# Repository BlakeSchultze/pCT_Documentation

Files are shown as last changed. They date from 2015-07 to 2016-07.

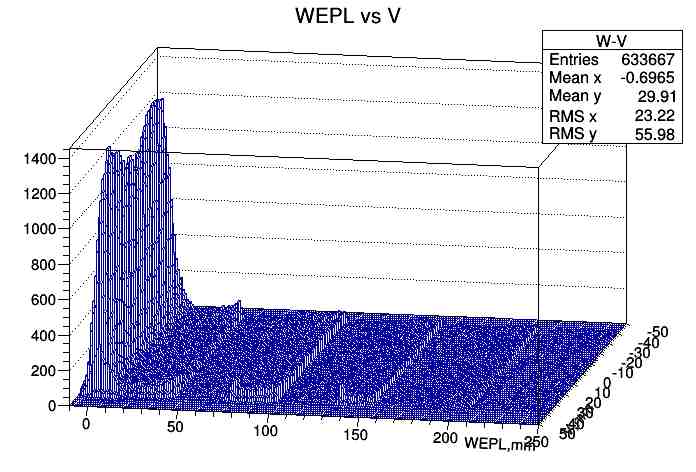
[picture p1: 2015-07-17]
Experimental_pCT_Runs/May 2015/preprocessing/WvsV1-1-1-1-4.5.jpg

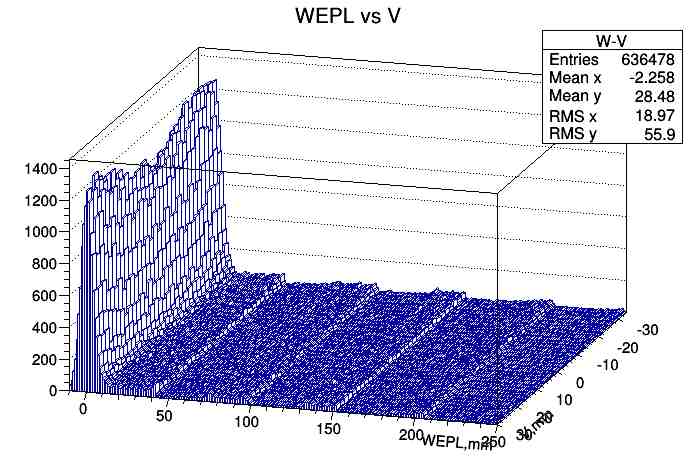
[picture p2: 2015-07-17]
Experimental_pCT_Runs/May 2015/preprocessing/WvsV1-2-3-4-5.jpg

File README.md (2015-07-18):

# pCT-Collaboration-Documents
======================================================
pCT Collaboration Document Sharing
======================================================
Contains the documentation associated with the pCT project such as descriptions of the scanner system and its operation as well as the various objects/phantoms that have or will be scanned.  This repository also includes the these/dissertations of students who worked on the project and publications from members of the collaboration or other outside groups on the subject of pCT or closely related topics.

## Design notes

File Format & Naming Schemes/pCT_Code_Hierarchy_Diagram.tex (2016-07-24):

%\newgeometry{left=1.25in,top=1.0in,bottom=-2in, paperwidth=4.3in,paperheight=4.4in,centering}
%top color=blue!2!white, middle color=blue!6!white, bottom color=blue!13!white
%\clearpage%
\Section{pCT\_code Hierarchy Diagram}[the diagram below shows the hierarchy of \docentry[constdir]{pCT\_code} directories including those containing clones of the GitHub accounts/repositories relevant to pCT.]%
\centering%
\begin{tikzpicture}[scale=4, font=\small,framed,background rectangle/.style={double, ultra thick, draw=stdblue, double=cyan, top color=stdblue!1!white, rounded corners=20pt}]
\matrix[row sep=4mm,column sep=2mm]
{%
&\node(parentdot)[pt]{};\\
&\node(01)[D]{ion};\\
&\node(11)[D]{pCT\_code};\\
\node(20)[pt]{};&\node(21)[pt]{};&&\node(23)[pt]{};\\
\node(30)[D]{user\_code};    &&&\node(33)[D]{git};\\[0mm]
%\node(01)[pt]{};&\node(top3)[pt]{};&\node(03)[pt]{};&&&\node(04)[pt]{};&&&\node(05)[pt]{};\\
\node(40)[D]{$<$username$>$};&\node(41)[pt]{};&\node(42)[pt]{};&\node(43)[pt]{};&&\node(45)[pt]{};\\
&\node(51)[D]{BlakeSchultze};&\node(52)[D]{BaylorICTHUS};&&&\node(55)[D]{pCT-collaboration};\\[1mm]
\node(60)[pt]{};&\node(61)[pt]{};&\node(62)[F]{pCT\_Reconstruction};&\node(63)[pt]{};&\node(64)[pt]{};&\node(65)[pt]{};&\node(66)[pt]{};&\node(67)[pt]{};\\[1mm]
\node(70)[F]{pCT\_Reconstruction};&\node(71)[F]{pCT\_Documentation};&&\node(73)[F]{pCT-docs};&\node(74)[F]{pCT\_Tools};&\node(75)[F]{Reconstruction\_BU};&\node(76)[F]{pct-recon-copy};&\node(77)[F]{Preprocessing};\\[1mm]
};
%\path[every node/.style={font=\sffamily\small}]
%       (parentdot) edge node (01)
%       (01) edge node {} (11)
%       (11) edge node {} (21)
%       (21) edge node {} (20)
%       (20) edge node {} (30)
%       (30) edge node {} (40);%
%%       (B) 	edge [loop left] node {0.0} (B)
%%           	edge [bend right] node [right] {0.0} (D)
%%           	edge [bend right] node[below] {0.0} (C)
%%       (C) 	edge [bend right] node [right] {0.0} (A)
%%           	edge [bend right] node [above] {0.0} (B)
%%           	edge [bend left] node [left] {0.0} (D)
%%           	edge [right] node [above] {0.0} (E)
%%       (D) 	edge [loop below] node {0.0} (D);
\graph [use existing nodes, edge label]
{
(parentdot)->(01)->(11)->(21)--(20)->(30)->(40);
(21)--(23)->(33)--(43)--(42)--(41)->(51)--(61)--(60)->(70);
(43)--(45)->(55)--(65)--(63)--(67)->(77);
(42)->(52)->(62);
(61)->(71);
(63)->(73);
(64)->(74);
(65)->(75);
(66)->(76);
};
\end{tikzpicture}
\endinput

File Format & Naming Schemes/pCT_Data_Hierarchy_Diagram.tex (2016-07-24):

\clearpage%
\Section{organized\_data Hierarchy Diagram}[the diagram below shows the hierarchy of \docentry[constdir]{organized\_data} directories where the vertical ellipses (\,$\vdots$\,) indicate the subdirectories of the experimental and simulated data scan date directories are identical.]
\centering%
%\newgeometry{left=1.25in,top=1.0in,bottom=-2in, paperwidth=4.3in,paperheight=4.4in,centering}
%top color=blue!2!white, middle color=blue!6!white, bottom color=blue!13!white
\begin{tikzpicture}[scale=4, framed,background rectangle/.style={double, ultra thick, draw=stdblue, double=cyan, top color=stdblue!1!white, rounded corners=20pt}]
\matrix[row sep=4mm,column sep=1mm]
{%
	&&&\node(parentdot)[pt]{};&&&&\\
	&&&\node(parentdir)[D]{ion};&&&&\\
	&&&\node(pctdata)[D]{pCT\_data};&&&&\\
	&&&\node(organizeddata)[D]{organized\_data};&&&&\\
	&\node(top1)[pt]{};&&\node(top3)[pt]{};&\node(top4)[pt]{};&&&\\
	&\node(001)[D]{Experimental};    &&&\node(004)[D]{Simulated};&\\[-2mm]
	&\node(01)[pt]{};&&\node(03)[pt]{};&\node(04)[pt]{};&\node(05)[pt]{};&&\\
	&\node(11)[D]{YY-MM-DD};        &&\node(13)[D]{G\_YY-MM-DD};&&\node(15)[D]{T\_YY-MM-DD};\\[1mm]
	&&&\node(0023)[textonly]{$\vdots$};&&\node(0025)[textonly]{$\vdots$};&&\\[-13mm]
	%&&&&&\\[-5mm]
	&\node(21)[D]{XXXX[\_AAA]};     &&\node(23)[textonly]{};&&\node(25)[textonly]{};\\[0mm]
	\node(30)[pt]{};&\node(31)[pt]{}; & \node(32)[pt]{};&&&\\
	\node(40)[D]{Input};       &&\node(42)[D]{Output};       &&&&\\
	\node(50)[F]{raw\_xxx.bin};&&\node(52)[D]{YY-MM-DD};     &&&&\\[-2mm]
	&\node(61)[pt]{};          &\node(62)[pt]{};    &\node(63)[pt]{};&\node(64)[pt]{};&\node(65)[pt]{};\\
	&\node(71)[F]{Wcalib.txt}; &\node(72)[D]{Reconstruction}; &\node(73)[F]{TVcorr.txt};   &\node(74)[F]{WcalibTemp.txt};&\node(75)[F]{projection\_xxx.bin};&&&&&&&&\\[-2mm]
	&				   &\node(82)[pt]{};&\node(83)[pt]{};&\\
	&                          &\node(92)[D]{YY-MM-DD};       &\node(93)[F]{settings.cfg};&&&&&&&&&&\\[-2mm]
	\node(100)[pt]{};&\node(101)[pt]{};&\node(102)[pt]{};    &\node(103)[pt]{};&\node(104)[pt]{};&\node(105)[pt]{};\\
	\node(110)[F]{hull.txt};&\node(111)[F]{FBP.txt};&\node(112)[D]{Images};&\node(113)[F]{x\_0.txt};&\node(114)[F]{TV\_measurements.txt};&\node(115)[F]{execution\_log.txt};
	&&&&&&&&\\
	&& \node(122)[D]{YY-MM-DD};\\[-2mm]
	&\node(131)[pt]{};&\node(132)[pt]{};&\node(133)[pt]{};&&\\
	&\node(141)[F]{x\_k.dcm};&\node(142)[F]{x\_k.txt};&\node(143)[F]{x\_k.png};&&&&&&&&&&\\
};
\graph [use existing nodes, edge label]
{
	(parentdot)->(parentdir)->(pctdata)->(organizeddata)--(top3)--(top1)->(001)--(01)->(11)->(21)--(31)--(30)->(40)->(50);
	(top3)--(top4)->(004)--(04)--(05)->(15)->(25);
	(04)--(03)->(13)->(23);
	(31)--(32)->(42)->(52)--(62)->(72)--(82)->(92)--(102)->(112)->(122)--(132)->(142);
	(61)--(62)--(63)--(64)--(65);
	(61)->(71);
	(62)->(72);
	(63)->(73);
	(64)->(74);
	(65)->(75);
	(82)--(83)->(93);
	(100)--(101)--(102)--(103)--(104)--(105);
	(100)->(110);
	(101)->(111);
	(102)->(112);
	(103)->(113);
	(104)->(114);
	(105)->(115);
	(131)--(132)--(133);
	(131)->(141);
	(132)->(142);
	(133)->(143)
};
\end{tikzpicture}
\endinput

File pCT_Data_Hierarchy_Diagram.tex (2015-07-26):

\documentclass[landscape,a4]{article}
\usepackage{mymacros}
%%%%%%%%%%%%%%%%%%%%%%%%%%%%%%%%%%%%%%%%%%%%%%%%%%%%%%%%%%%%%%%%%%%%%%%%%%%%%%%%%%%%%%%%%%%%%%%%%%%%%%%%%%%%%%%%%%%%%%%%%%%%%%%%%%%%%%%%%%%%%%%%%%%%%%%%%%%%%%%%%%%%%%%%%%%%%%%%%%%%%%%%%%%%%%%%%%%%%%%%%%%%%%%%%%%%%%%%%%%%%%
%%%%%%%%%%%%%%%%%%%%%%%%%%%%%%%%%%%%%%%%%%%%%%%%%%%%%%%%%%%%%%%%%%%%%%%%%%%%%%%%%%%%%%%%%%%%%%%%%%%% Document Body %%%%%%%%%%%%%%%%%%%%%%%%%%%%%%%%%%%%%%%%%%%%%%%%%%%%%%%%%%%%%%%%%%%%%%%%%%%%%%%%%%%%%%%%%%%%%%%%%%%%%%%%%%%
%%%%%%%%%%%%%%%%%%%%%%%%%%%%%%%%%%%%%%%%%%%%%%%%%%%%%%%%%%%%%%%%%%%%%%%%%%%%%%%%%%%%%%%%%%%%%%%%%%%%%%%%%%%%%%%%%%%%%%%%%%%%%%%%%%%%%%%%%%%%%%%%%%%%%%%%%%%%%%%%%%%%%%%%%%%%%%%%%%%%%%%%%%%%%%%%%%%%%%%%%%%%%%%%%%%%%%%%%%%%%%
\begin{document}
%%%%%%%%%%%%%%%%%%%%%%%%%%%%%%%%%%%%%%%%%%%%%%%%%%%%%%%%%%%%%%%%%%%%%%%%%%%%%%%%%%%%%%%%%%%%%%%%%%%%%%%%%%%%%%%%%%%%%%%%%%%%%%%%%%%%%%%%%%%%%%%%%%%%%%%%%%%%%%%%%%%%%%%%%%%%%%%%%%%%%%%%%%%%%%%%%%%%%%%%%%%%%%%%%%%%%%%%%%%%%%
%%%%%%%%%%%%%%%%%%%%%%%%%%%%%%%%%%%%%%%%%%%%%%%%%%%%%%%%%%%%%%%%%%%%%%%%%%%%%%%%%%%%%%%%%% Create Title Page With Graphics %%%%%%%%%%%%%%%%%%%%%%%%%%%%%%%%%%%%%%%%%%%%%%%%%%%%%%%%%%%%%%%%%%%%%%%%%%%%%%%%%%%%%%%%%%%%%%%%%%%
%%%%%%%%%%%%%%%%%%%%%%%%%%%%%%%%%%%%%%%%%%%%%%%%%%%%%%%%%%%%%%%%%%%%%%%%%%%%%%%%%%%%%%%%%%%%%%%%%%%%%%%%%%%%%%%%%%%%%%%%%%%%%%%%%%%%%%%%%%%%%%%%%%%%%%%%%%%%%%%%%%%%%%%%%%%%%%%%%%%%%%%%%%%%%%%%%%%%%%%%%%%%%%%%%%%%%%%%%%%%%%
\tikzset{fontscale/.style = {font=\relsize{#1}}
    }
    \begin{tikzpicture}[
%%%%%%%%%%%%%%%%%%%%%%%%%%%%%%%
D/.style={
% The shape:
rectangle,
% The size:
minimum size=1pt,
% The border:
very thick,
draw=green!50!black!50, % 50% red and 50% black,
% and that mixed with 50% white
% The filling:
top color=white, % a shading that is white at the top...
bottom color=green!50!black!20, % and something else at the bottom
% Font
font=\itshape\tiny
},
%%%%%%%%%%%%%%%%%%%%%%%%%%%%
F/.style={
% The shape:
rectangle,
rounded corners=5pt,
% The size:
minimum size=1mm,
% The border:
very thick,
draw=green!50!black!50, % 50% red and 50% black,
% and that mixed with 50% white
% The filling:
top color=white, % a shading that is white at the top...
bottom color=blue!50!black!20, % and something else at the bottom
% Font
font=\itshape\tiny
},
%%%%%%%%%%%%%%%%%%%%%%%%%%%%%%
end/.style={
% The shape:
rectangle,
rounded corners=5pt,
% The size:
minimum size=4mm,
% The border:
very thick,
draw=green!50!black!50, % 50% red and 50% black,
% and that mixed with 50% white
% The filling:
top color=white, % a shading that is white at the top...
bottom color=red!50!black!20, % and something else at the bottom
% Font
font=\itshape\tiny
},
%%%%%%%%%%%%%%%%%%%%%%%%%%%%%%%%%%%%%%%%
,>=stealth',thick,black!50,text=black,
every new ->/.style={shorten >=0pt},
graphs/every graph/.style={edges=rounded corners},
%%%%%%%%%%%%%%%%%%%%%%%%%%%%%%%%%%%%%%%%%%%%%%%%%%%%%%%%%
pt/.style={draw,inner sep=0pt,minimum size=0.3pt,fill=black!50},
%%%%%%%%%%%%%%%%%%%%%%%%%%%%%%%%%%%%%%%%%%%%%%%%%%%%%%%%%%%%%%%%%%%
skip loop/.style={to path={-- ++(0,#1) -| (\tikztotarget)}}]
\matrix[row sep=3mm,column sep=1mm]
{\tiny
                           &&&&&&&\node(013)[D]{pCT Data};    &&&&&&                       &&\\[0mm]
                           &&\node(20)[pt]{};                 &&&&&&&\node(213)[pt]{};     &&&&&&\node (23)[pt]{};            &&\\
                           &\node(30)[D]{Experimental};       &&&&&&&                      &&&&&&\node(33)[D]{Simulated};   &&\\
                           &\node(40)[D]{YY-MM-DD(Run Date)}; &&&&&&&                      &&&&&&&&\\[-1mm]
                           &\node(50)[D]{XXXX[\_AAA](Run\#)}; &&&&&&&                      &&&&&&&&\\
\node(60)[D]{Input};       &&\node(50)[D]{Output};            &&&&&&&                      &&&&&&&&\\
\node(60)[F]{raw\_xxx.bin};&&\node(50)[D]{YY-MM-DD};          &&&&&&&                      &&&&&&&&\\
&\node(60)[F]{Calib.txt};  &\node(50)[F]{projection\_xxx.bin};&\node(613)[F]{settings.cfg};&\node(613)[D]{Reconstruction};&&&&&&&&\\
&                          &                                  &                            & \node(613)[D]{YY-MM-DD};  &&&&&&&&&\\
&\node(50)[F]{hull.txt};   &\node(613)[F]{FBP.txt};           &\node(613)[F]{x\_0.txt};    &\node(613)[F]{MLP.bin};    &\node(613)[F]{histories.bin};&\node(50)[D]{Images};&&&&&&&\\
&                          &                                  &                            &                           &                            & \node(613)[D]{YY-MM-DD}; &&&&&;            &&\\
&                          &                                  &                            &                           & \node(613)[F]{DICOM};   & \node(613)[F]{TEXT}; &\node(613)[F]{PNG};&&&&;            &&\\
};
%\matrix[row sep=5mm,column sep=1mm]
%{
%    \node (t) [task] {Established Tasks};\\
%    \node (d) [development] {Newly ProposedIn Development};\\
%    \node (r) [remove] {Potentially Replace};
%};
\graph [use existing nodes, edge label]
{
};

\end{tikzpicture}

\end{document}

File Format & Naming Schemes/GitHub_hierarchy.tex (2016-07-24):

%\clearpage%
\Section{GitHub Accounts/Repositories}
\begin{tcbenvironment}'tcbBlueStyle'[title=\shadowText{GitHub}]
%%%%%%%%%%%%%%%%%%%%%%%%%%%%%%%%%%%%%%%%%%%%%%%%%%%%%%%%%%%%%%%%%%%%%%%%%%%%%%%%%%%%%%%%%%%%%%%%%%%%%%%%%%%%%%%%%%%%%%%%%%%%%%%%%%%%%%%%%%%%%%%%%%%%%%%%%%%%%%%%%%%%%%%%%%%%%%%%%%%%%%%%%%%%%%%%%%%%%%%%%%%%%%%%%%%%%%%%%%%%%%
\begin{tcbparagraph}'tcbBlueStyle'(title=https:\dirsep\dirsep github.com\dirsep\caratenclosed*{GitHub account}\dirsep\caratenclosed*{GitHub repository})
$\boldsymbol{-}$ below is an outline of the GitHub accounts and repositories containing the source code for the various tools and programs relevant to pCT and the documentation for pCT software/hardware, code/data storage and management, collaborator projects and contact information, phantom naming and properties, and other useful information for pCT users.  To provide users with easy/direct access to the source code in these repositories, they are cloned to Kodiak/Tardis and stored according to the organizational scheme shown in \autohyperlink[type=Section]{Code Organization}.
\end{tcbparagraph}
%%%%%%%%%%%%%%%%%%%%%%%%%%%%%%%%%%%%%%%%%%%%%%%%%%%%%%%%%%%%%%%%%%%%%%%%%%%%%%%%%%%%%%%%%%%%%%%%%%%%%%%%%%%%%%%%%%%%%%%%%%%%%%%%%%%%%%%%%%%%%%%%%%%%%%%%%%%%%%%%%%%%%%%%%%%%%%%%%%%%%%%%%%%%%%%%%%%%%%%%%%%%%%%%%%%%%%%%%%%%%%
\begin{tcbparagraph}'tcbBlueStyle'{tcbenumeratedStyle}
\begin{ThinEnum}[parsep=1mm]
	\item \docentry[gitaccount]{pCT-collaboration} : contains repositories for pCT data acquisition, simulation, preprocessing, and reconstruction software and documentation describing the software/hardware, management of code/data, and other information relevant to pCT (e.g. collaborator list, hardware descriptions, phantom properties, etc.).
	\begin{ThinEnum}[parsep=1mm]
		\item \docentry[gitrepo]{pCT\_Tools} : contains bash functions/scripts and other tools useful for navigating data/code and configuring/running programs on Kodiak and Tardis compute nodes (along with documentation describing them and their purpose/usage) including a default \docentry[script]{\texttt{.bash\_profile}} which sources \docentry[script]{\texttt{pct\_user\_script.sh}} to configure user sessions for the current host/node and \docentry[script]{\texttt{load\_pct\_functions.sh}} to automatically load the aforementioned bash functions useful during a user terminal session.
		\item \docentry[gitrepo]{pCT-docs} : contains documentation on the pCT data/code naming and organizational scheme, collaborator's project involvement and contact info, and phantom properties/manuals/naming (including relevant subcategory tags).  The importance and naming of additional documentation from the original \docentry[gitrepo]{BlakeSchultze\dirsep pCT\_Documentation} repository are currently being evaluated for migration.
		\item \docentry[gitrepo]{pypct} : Python helpers for proton CT
		\item \docentry[gitrepo]{pct-acquire} : Proton CT data acquisition software for the Phase 2 pCT scanner system
		\item \docentry[gitrepo]{pct-sim} : GEANT4 program for simulating scans with the Phase 2 pCT scanner system
		\item \docentry[gitrepo]{Preprocessing} : program for preprocessing raw data to calculate tracker plane coordinates from tracker chip/channel/strip values and generate calibrated WEPL values from energy detector measurements.
		\item \docentry[gitrepo]{pct-recon-copy} : original Penfold/Hurley pCT reconstruction program now with a \docentry[gitbranch]{Baylor} branch configuring the \docentry[script]{Makefile} for Tardis execution and input/output directory execution parameters required for batch script submission of reconstruction job(s) to the GPU execution queue.
		\item \docentry[gitrepo]{Reconstruction\_BU} : contains only the current and previous release versions of Baylor's reconstruction program as developed in \docentry[gitaccount]{BaylorICTHUS\dirsep pCT\_Reconstruction} (no code development is performed here).
	\end{ThinEnum}
%%%%%%%%%%%%%%%%%%%%%%%%%%%%%%%%%%%%%%%%%%%%%%%%%%%%%%%%%%%%%%%%%%%%%%%%%%%%%%%%%%%%%%%%%%%%%%%%%%%%%%%%%%%%%%%%%%%%%%%%%%%%%%%%%%%%%%%%%%%%%%%%%%%%%%%%%%%%%%%%%%%%%%%%%%%%%%%%%%%%%%%%%%%%%%%%%%%%%%%%%%%%%%%%%%%%%%%%%%%%%%
\newpage
%%%%%%%%%%%%%%%%%%%%%%%%%%%%%%%%%%%%%%%%%%%%%%%%%%%%%%%%%%%%%%%%%%%%%%%%%%%%%%%%%%%%%%%%%%%%%%%%%%%%%%%%%%%%%%%%%%%%%%%%%%%%%%%%%%%%%%%%%%%%%%%%%%%%%%%%%%%%%%%%%%%%%%%%%%%%%%%%%%%%%%%%%%%%%%%%%%%%%%%%%%%%%%%%%%%%%%%%%%%%%%
%%%%%%%%%%%%%%%%%%%%%%%%%%%%%%%%%%%%%%%%%%%%%%%%%%%%%%%%%%%%%%%%%%%%%%%%%%%%%%%%%%%%%%%%%%%%%%%%%%%%%%%%%%%%%%%%%%%%%%%%%%%%%%%%%%%%%%%%%%%%%%%%%%%%%%%%%%%%%%%%%%%%%%%%%%%%%%%%%%%%%%%%%%%%%%%%%%%%%%%%%%%%%%%%%%%%%%%%%%%%%%
	\item \docentry[gitaccount]{BaylorICTHUS} : Baylor's pCT programs, tools, and documentation.
	\begin{ThinEnum}[parsep=1mm]
		\item \docentry[gitrepo]{pCT\_Reconstruction} : used in developing the release version of Baylor's pCT reconstruction program and containing branches for each of Baylor's pCT developers (Blake, Paniz, Sarah, ...) for independent development relevant to their work.  Developments made in a developer branch and proposed for integration in the next release version go through a review and testing process to verify the code and its impact on the full program.  Developments passing this verification process are then merged into the \docentry[gitbranch]{release\_development} branch.  When critical developments are merged into the \docentry[gitbranch]{release\_development} branch, this branch is then merged into the \docentry[gitbranch]{release} branch and the resulting code is then pushed to the \docentry[gitrepo]{pCT-collaboration\dirsep Reconstruction\_BU} repository, as this is the source for pCT users to acquire the current and previous release versions of the program.
	\end{ThinEnum}
%%%%%%%%%%%%%%%%%%%%%%%%%%%%%%%%%%%%%%%%%%%%%%%%%%%%%%%%%%%%%%%%%%%%%%%%%%%%%%%%%%%%%%%%%%%%%%%%%%%%%%%%%%%%%%%%%%%%%%%%%%%%%%%%%%%%%%%%%%%%%%%%%%%%%%%%%%%%%%%%%%%%%%%%%%%%%%%%%%%%%%%%%%%%%%%%%%%%%%%%%%%%%%%%%%%%%%%%%%%%%%
	\item \docentry[gitaccount]{BlakeSchultze} : parent directory for all pCT code/data on Kodiak and the Tardis compute nodes
	\begin{ThinEnum}[parsep=1mm]
		\item \docentry[gitrepo]{LaTeX-Packages} : provides the package \docentry![file]{my-latex.sty} which is included in TeX documents to provide access to the definitions of new commands/macros/environments, load the external/3rd-party package dependencies, and configure the typesetting of LaTeX documents as well as providing the collection of LaTeX style (.sty) and other files included in this repository upon which these definitions/configurations are dependent.
		\item \docentry[gitrepo]{pCT\_Documentation} : contains an expanded set of pCT documentation files with additional resources not included in the \docentry[gitrepo]{pCT-collaboration\dirsep pCT-docs} repository, such as pCT publications and theses/dissertations.
		\item \docentry[gitrepo]{pCT\_Reconstruction} : the original repository in which Baylor's pCT reconstruction program was developed, which also contains the experimental development of an alternative program configuration with several automated routines, and is currently being merged into the release version of Baylor's reconstruction program as provided in \docentry[gitrepo]{BaylorICTHUS\dirsep pCT\_Reconstruction}.
		\item \docentry[gitrepo]{WED\_Analysis} : provides tool for determining the water-equivalent depth (WED) for a set of beam-aim point (BAP) coordinates based on reconstructed image RSP values, using the voxel walk algorithm developed as part of the pCT reconstruction program.  This algorithm steps from voxel edge to voxel edge along a trajectory to determine exact voxel intersection coordinates and prevent the missing of small voxel intersections which can occur when taking constant length steps along a path as was done in the original reconstruction program.
	\end{ThinEnum}
\end{ThinEnum}
\end{tcbparagraph}
%\par\bigskip\bigskip\bigskip\bigskip\bigskip\smallskip
\end{tcbenvironment}

%\clearpage

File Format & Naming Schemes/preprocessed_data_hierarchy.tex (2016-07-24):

\clearpage%
\Subsection{Preprocessed Data Hierarchy}
\begin{tcbenvironment}'tcbBlueStyle'[title=\shadowText{preprocessed\_data}]
%%%%%%%%%%%%%%%%%%%%%%%%%%%%%%%%%%%%%%%%%%%%%%%%%%%%%%%%%%%%%%%%%%%%%%%%%%%%%%%%%%%%%%%%%%%%%%%%%%%%%%%%%%%%%%%%%%%%%%%%%%%%%%%%%%%%%%%%%%%%%%%%%%%%%%%%%%%%%%%%%%%%%%%%%%%%%%%%%%%%%%%%%%%%%%%%%%%%%%%%%%%%%%%%%%%%%%%%%%%%%%
\begin{tcbparagraph}'tcbBlueStyle'(title=\dirsep ion\dirsep pCT\_data\dirsep preprocessed\_data)%[title=\dirsep ion\dirsep pCT\_data\dirsep preprocessed\_data\dirsep$\dots$]
$\boldsymbol{-}$ directory containing the preprocessed experimental data organized by scan and processed dates
\end{tcbparagraph}
%%%%%%%%%%%%%%%%%%%%%%%%%%%%%%%%%%%%%%%%%%%%%%%%%%%%%%%%%%%%%%%%%%%%%%%%%%%%%%%%%%%%%%%%%%%%%%%%%%%%%%%%%%%%%%%%%%%%%%%%%%%%%%%%%%%%%%%%%%%%%%%%%%%%%%%%%%%%%%%%%%%%%%%%%%%%%%%%%%%%%%%%%%%%%%%%%%%%%%%%%%%%%%%%%%%%%%%%%%%%%%
\begin{tcbparagraph}'tcbBlueStyle'{tcbenumeratedStyle}
	\begin{ThinEnum}[labelindent=1pt, leftmargin=*]
	    \item \docentry[dir]{YY-MM-DD} : Folder containing all processed experimental data corresponding to the raw experimental data acquired on \docentry![subcategory]{YY-MM-DD}
	    \begin{ThinEnum}[labelindent=1pt, leftmargin=*]
	        \item \docentry[dir]{YY-MM-DD} : Folder containing all processed experimental data generated on \docentry![subcategory]{YY-MM-DD} from the raw data
	        \begin{ThinEnum}[labelindent=1pt, leftmargin=*]
	            \item \docentry[file]{TVcorr.txt} : contains TV corrected WEPL calibration curve coefficients.
			\item \docentry[file]{WcalibTemp.txt} : temporary file containing WEPL calibration curve coefficients.
			\item \docentry[file]{Wcalib.txt} : contains final WEPL calibration curve coefficients.
			\item \docentry[fileset]{$<$Phantom$>$\_XXXX[\_AAA]\_xxx.dat.root.reco.root.bin} : processed experimental data with tracker coordinates, recovery of missing hits when possible, and calibrated WEPL measurements for the object named \docentry![subcategory]{$<$Phantom$>$}, from run \# \docentry![subcategory]{XXXX[\_AAA]}, where \docentry![subcategory]{XXXX} is a 4 digit \# with leading zeros and \docentry![subcategory]{\_AAA} is an optional descriptor tag, and \docentry![subcategory]{xxx} is the gantry angle at which the data was acquired.
	        \end{ThinEnum}
	    \end{ThinEnum}
	\end{ThinEnum}
\end{tcbparagraph}
\end{tcbenvironment}
\endinput

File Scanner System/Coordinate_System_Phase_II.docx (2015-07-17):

# Phase 2 pCT Scanner Coordinate Systems

# Overview

Two coordinate systems and the relation between them are defined for pCT (Fig. 1). First is the reconstruction coordinate system. This system is fixed relative to the imaging subject. For a head scan with the object in a standard supine, head first position (lying on the back, head into the scanner), the axes of the reconstruction coordinate system are defined with respect to anatomical directions following the DICOM standard described in PS 3.3 – 2011 [1]. Note that this does not conflict with placing the imaging subject differently than the standard position, e.g. prone. The second system is the detector coordinate system. In a typical tomographic scanner, this system rotates around the reconstruction system in a clockwise direction from 0 degree to 360 degree, from the perspective of an observer on the floor, but does not translate relative to it. This means that origin of both systems coincide.

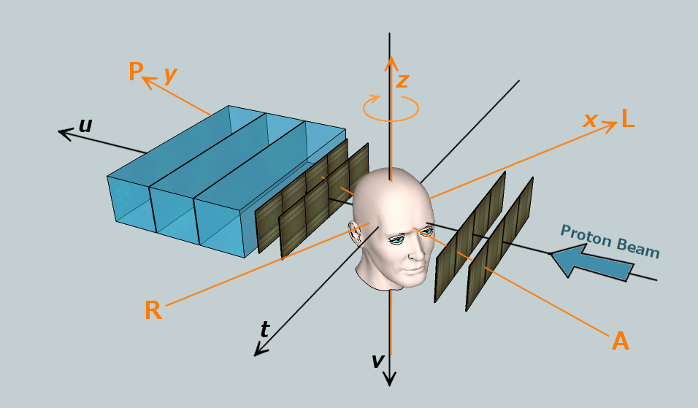
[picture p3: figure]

Fig. 1. Phase 2 scanner coordinate systems. The orange coordinate axes correspond to the reconstruction coordinate system and the black axes to the detector coordinate system. In the Phase 2 scanner, the imaged object (phantom) rotates as shown by the orange arrow, i.e. in clockwise direction when viewed from above.

# Reconstruction system (x, y, z)

For a nominal patient scan, a patient orientation of "supine" and "head-first" is assumed. In this orientation, the x-axis is the R-L anatomical axis, the y-axis is the A-P anatomical axis, and the z-axis is the I-S anatomical axis. The origin of this system is the center of the reconstruction volume, which is defined more rigorously by the intersection of the rotational axis of the rotation stage (perpendicular to u and t) and the orthogonal plane that intersects the center of the detectors (in v). The typical rendering of the reconstructed images should be viewed from negative towards positive z, with the x-axis horizontal and the y-axis vertical. In the DICOM convention, the positive x-axis points towards the anatomical left of the patient, and the positive y-axis points to the anatomical posterior direction. This is a right-handed coordinate system.

# Detector system (t, u, v)

This system is defined by the proton beam axis and the pCT detectors. The origin of this system shares the point in space with the origin of the reconstruction system. The positive t-axis points towards the left of the observer when looking in proton beam direction, the positive u-axis points in beam direction, and the positive v-axis is defined by the fact that t, u, v is a right-handed coordinate system. The rotation of the detector system relative to the reconstruction system is around the z-axis and follows the right-hand-rule, i.e., the detectors rotate counterclockwise when the observer is looking towards the negative z-axis. If the detector system is fixed, as is the case for the Phase 2 scanner, the phantom rotates clockwise around the detector v-axis when looking towards the positive v-axis, thus likewise following the right-hand rule. At 0 degrees, the u-axis (beam axis) points in the direction of the positive y-axis, and the t-axis points in the direction of the negative x-axis. In other words, when a head is scanned in standard orientation (supine, head first) it will be facing the beam.

# Phase 2 scanner orientation

The Phase 2 scanner will be mounted such that the head phantom is upright (the superior (z-) axis points towards the ceiling) and the rotational stage axis is vertical. For the 0-degree position of the rotational stage, the phantom will be facing the front detector module and the beam, and the top of the head will point to the ceiling. The head will then rotate clockwise when viewed down from the ceiling (in negative z-axis direction). The same scan in the future gantry-mounted scanner (Phase 3) will have the patient lying on their back (supine) with the head going into the gantry (head-first). At gantry rotation of 0 degrees, the beam delivery system (nozzle) will be at its highest position and the beam axis will point down in posterior direction of the patient. The gantry will then rotate clockwise when the observer is facing it. From the point of view of image reconstruction, the Phase 2 and 3 arrangements will be identical and conform to DICOM standard.

# References

1. Digital Imaging and Communications in Medicine (DICOM). http://medical.nema.org/standard.html

pCT Collaboration March 15, 2014

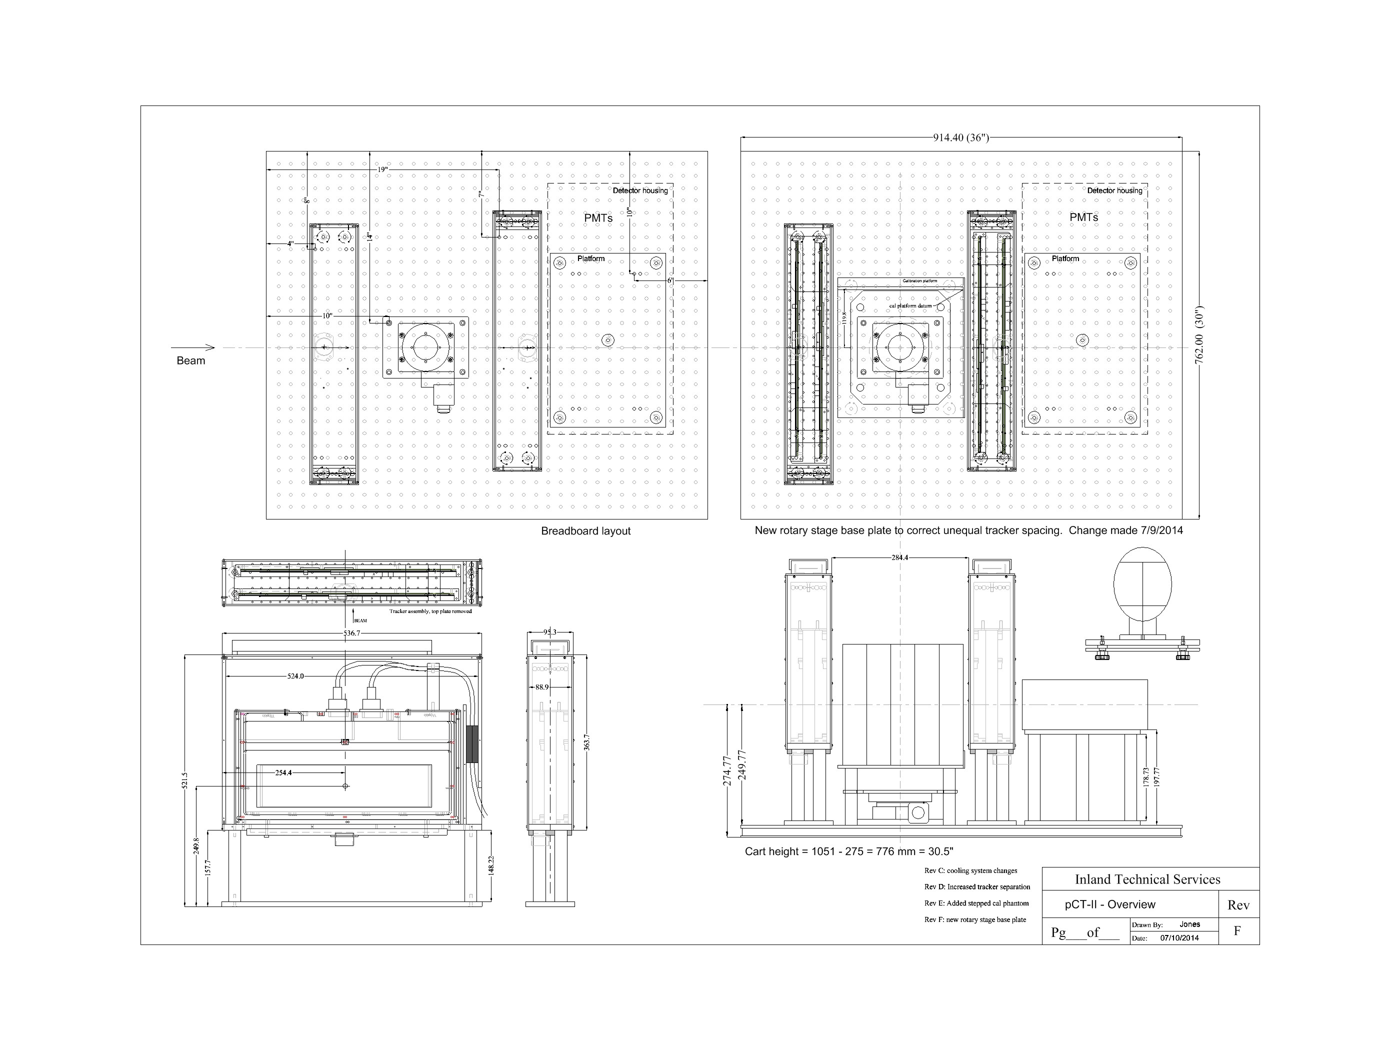
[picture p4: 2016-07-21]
Scanner System/pCT-II overview.jpg

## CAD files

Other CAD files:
Format & Naming Schemes/pCT_Data_Hierarchy.dwg

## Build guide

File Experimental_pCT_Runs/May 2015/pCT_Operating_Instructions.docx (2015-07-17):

May 11, 2015

Robert Johnson

# pCT Phase-II Scanner Operation

# Installation and Cabling Setup

In the following, use cable ties to secure the various signal cables, high voltage cables, USB cables, Ethernet cable, etc. to the scanner structure, to avoid damage if somebody trips over a cable.

1. Set up the data acquisition computer, its monitor, its mouse, and its keyboard in the radiation-safe area. Two cables will run from it to the scanner. Probably they will have to run under the door.
2. Install the energy detector from the rear onto its table under the electronics of the scanner, taking care to clear the various cables. The lemo plugs must be on the left (when looking toward the beamline) and pointing downward. Scoot the enclosure all the way forward and to the left, such that the ridge around the enclosure pushes up against the table. Check the left-right position to verify that the energy detector window matches the tracker window.
3. Plug in the 5 energy detector signal cables according to the channel labels on the detector and on the cables, and then plug in the high-voltage cable.
4. Position the scanner properly relative to the beam line, making sure that the height is correct to put the beam into the center of the aperture. Lock it into place if possible, and then measure and log the distance from the beam source and the front of the tracker.
5. Plug in the long white AC-power extension cord and position its outlets close to the scanner. Plug the black extension cord into the white one or into another outlet.
6. Plug the blower rheostat into the black extension cord. The rheostat on/off switch should be tapes into the on position. Plug the blower into the rheostat, and then attach the blower hoses to the fittings on the bottoms of the two tracker enclosures. Make sure that the hoses do not interfere with the stage.
7. Plug the event builder 12V AC power adapter into the white extension cord and then into the event builder ML605 board (a white connector on the top of the board). Try to avoid bending the board when plugging it in. Making this connection first (and removing it last) is helpful in grounding all of the electronics and thus reducing susceptibility to electrostatic discharge.
8. Position the following auxiliary boxes close to the scanner and attach an AC power cord to each:
  a. Two black BKPRECISION switching power supplies.
  b. The Sorensen XEL supply for the tracker bias.
  c. The energy detector ISEG high-voltage supply.
  d. The stage controller.
9. Connect the energy detector high voltage cable to the ISEG power supply. To avoid damage they must connect to the correct channels! The -365 volts goes to the left channel (when facing the front of the supply) while the -800 volts goes to the right channel. Don’t do this if you are unsure, as applying the -800 volts to the wrong cable will surely destroy all of the transistors and zener diodes on the PMT bias board inside of the energy detector.
10. Plug the BKPRECISION power cords into the black extension cord. This is important to ensure that the tracker power cannot be turned on without turning on the blower.
11. Plug the other boxes into the white extension cord.
12. Connect the cable from the stage controller to the stage.
13. Connect the tracker bias cable from the Sorensen XEL supply to the mezzanine board. On the supply end the cable has banana plugs, red to the high voltage and black to ground. The plug on the mezzanine board is clearly labeled and marked with red tape. It is crucial not to plug this into the tracker or energy detector power plugs. The 100V bias would surely destroy the electronics!
14. Connect the energy detector power cable (thinner 4-wire grey cable attached to one of the BKPRECISION supplies) to the top crowbar box that is in turn plugged into the mezzanine board.
15. Connect the tracker power cable (thicker 4-wire grey cable attached to one of the BKPRECISION supplies) directly into the mezzanine board. (While the lower crowbar box is meant to be for the tracker, in practice it does not work well enough for operation outside of the UCSC lab. The 18-amp fuse will not blow when the crowbar trips, because the supply cannot source more than 22 amps, which apparently is not enough. At the same time, the 16 or 17 amps drawn by the tracker heats up the fuse a lot and produces too much voltage drop across it.)
16. Set up the white USB hub close to the scanner and plug its power converter into the white extension cord. Plug its white input cable into the end of the 50-foot active USB cable, and plug the USB cable’s power converter into the white extension cord. Note that these two power converters are interchangeable. Run the 50-foot USB cable all the way to the data acquisition PC. Cable tie all of this into place to secure it.
17. Run a USB cable from the hub to the event builder. The event-builder end is a mini-connector. There are two jacks, one for programming and the other for the UART connection. Here we want the UART connection. There is a small label on the board, but it can also be recognized as the USB jack that is closest to the mezzanine interface board.
18. Run USB cables from the hub to the two BKPRECISION supplies, the Sorensen XEL supply, the ISEG high-voltage supply, and the stage controller.
19. Run a long Cat-5 Ethernet cable from the little Ethernet board mounted onto the event-builder mezzanine board to the data-acquisition computer. On the back of the computer it should plug into the lower Ethernet adapter (the upper one is for network connections).
20. Turn on the power strip of the white extension cable.

(I’m assuming that no beam-phase-lock will be used for the energy detector digitizer clocks. Otherwise the beam RF coax cable would have to be plugged into the lemo connector of the mezzanine board and a USB cable from a PC would have to be plugged into the same board in order to program the chip that does the phase lock and generates the digitizer clock.)

# System Startup

Turn on the system power as follows:

1. The power strip into which the blower rheostat and tracker power supplies are plugged is turned on first. You should then hear the blower. Do not proceed to turn on the tracker power without the blower running (with the air hoses plugged into the two tracker modules, of course).
2. Turn on the event builder (Xilinx ML605 board). The switch is partially obscured by our mezzanine interface board, so a small stick may be needed in order push the switch.
3. Turn on the Tracker and Energy-Detector power supplies (two black BKPRECISION boxes with switches on the back), the Tracker bias power supply (Sorensen XEL supply with the power switch on the front), and the Energy Detector PMT high-voltage supply (ISEG supply with the switch on the back).
4. Turn on the controller for the stage (switch on the back).
5. Type “python /home/daq/powerSupplyGUI/powersupplyGUI.py” This should open up a GUI window for operating the power supplies. It is supposed to connect automatically to all of the supplies over USB. If it bombs you can try power cycling the relevant supply and then try the GUI again.
6. Using the GUI pull-down menus, turn on the tracker and energy detector supplies. You should see a voltage of 5.5V for the energy detector and 5.0V for the tracker. If not, use the menus to set them so. The tracker should show a current of around 3.5 amps while the energy detector should show about 1.3 amps.
7. On the PMT HV supply, switch on the two front-panel switches to enable the HV output. Make sure that the voltage setting is negative and that the left channel reads about -365V while the right channel reads about -800V.
8. Using the power GUI turn on the tracker bias voltage. Use the GUI to set the voltage to 100V.

Monitor the tracker and energy detector voltages and currents as follows:

1. Type “python /home/daq/powerSupplyGUI/powerMonitorGUI.py”. You should see a large GUI window open and display the voltages and currents on each of the 8 tracker boards and the two energy-detector digitizer boards.
2. Click on the checkbox at the bottom left to turn on the tracker ASIC power. You should then see voltage and current for every supply. You should also see on the power supply GUI that the tracker current increases to between 16 and 17 amps.
  a. Check that each supply on each board is close to the expected voltage (1.2V, 1.8V, 2.1V, 2.5V, or 3.3V).
  b. Check that boards of the same type are drawing about the same amount of current for each supply. Note that you will not see current from the 1.8V supplies, as those only supply current during the FPGA programming.
  c. Check the bias current readings for the V boards, but ignore the T-board bias current readings (they are internally disconnected to solve a noise problem). You can expect a few hundred micro-amps per board, but you will see the current steadily rise as time progresses. Mainly you want to verify that the currents are zero.
  d. Check that the temperatures look reasonable (near room temperature if you just recently turned the system on, but in any case well below 40C).
3. Click the ASIC current off.
4. Delete the monitor window. It cannot operate simultaneously with the data acquisition program.

Note that the tracker and energy detectors must be powered on after the event builder is powered on. That is because the event builder FPGA must be operating before booting the FPGAs on the tracker and detector boards. So if you power cycle the event builder you must then power cycle the detector boards.

# Configuration Setup

Open the file /home/daq/git/pct-acquire/pct_config.yaml in an editor (e.g. gedit). Keep it open during the beam test, for convenience. Make sure that the following parameters are set properly (since these often get changed around for testing purposes):

- event_builder:
  - timepix: false
  - spill_synch: false (unless operating at LLU, in which case true may be desired)
  - tracker_trigger_mask: 0
  - energy_trigger_mask: 1
  - tracker: asic_default: trigger_delay: 2
  - energy_detector:
    - data_type: reduced
    - sample_config: [6, 8]
    - trigger_delay: 7
- scan_config: (all of these may be set by hand from the GUI)
  - starting_run_number: (usually this is set by hand for each run; 0 is a good default to prevent overwriting data in case you forget to set the run number)
  - filename_pattern: (set this to point to the SSD area for data acquisition)
  - max_seconds: 20 (decrease or increase according to the maximum run time desired for each stage angle)
  - max_bytes: 200000 (this is what normally stops the run at each angle)
  - start_angle: 0
  - stop_angle: 360 (for a full scan)
  - angle_step: 4

You may want to change the “monitor_supplies” and “monitor_temperature” settings on the various boards. If set “true” they will result in the system reading the supply voltages and/or temperatures of the boards during the configuration stage prior to a run, with the results displayed on the pct-acquire GUI. The reading is rather slow, however, so that having all or many of them set “true” greatly slows down the configuration process.

# Executing a Scan

Make sure that everything is powered on, including the tracker bias! Start the pct-acquire from the folder “/home/daq/pct-acquire/” by the command

./pct.py log-file-name

where the log-file name should include the starting run number for the scan and ideally should be located in the SSD area where the data are sent. You should see the pct-acquire GUI window pop open. To start a scan going, do the following:

1. Click on the “Control Stage” button. If this is the first run of the session, click “Home” and wait for the stage to rotate one way and then the other until it says that it is homed. If the program cannot connect to the stage, you may have to power cycle the stage controller, restart the GUI, and try again.
2. Click on the “Configure Detectors” button. It will then take a while to go through the configuration sequence. While it is doing so you can work on the next step.
3. Set up the scan configuration:
  a. Set the “Starting run number” to a unique value for the beam test and write the number in the log book.
  b. Make sure that the “Filename Pattern” is correct. It should start with the SSD folder location for data from the current beam test followed by a descriptor of the run, such as “Emp” for an empty run, “Cal” for WEPL calibration, or the name of a phantom. Then should follow patterns for the run number and stage angle.
  c. “Max Seconds” and “Max Bytes” determine when the run will stop. 200,000 bytes will give around 4 million events. (Note that usually by the time the system notices that the byte count has exceeded Max Bytes and manages to halt the run the system has accumulated a few more tens of millions of events.)
  d. Make sure that the stage start, stop, and step values correspond to what is desired for the scan.
4. Once the configuration is complete, check the “Supply Monitor” readings, if there are any. You may need to click the “Reset Ethernet” button, especially if the previous run was aborted without closing everything down properly. If the system fails to link of with the event builder over Ethernet, then you will have to exit the GUI and start over. Hitting the reset doesn’t cost much time and can prevent connection problems.
5. Finally, click the “Start Scan” button.

During the run the GUI will display the bytes accumulated and bytes written to disk. When the run terminates for a given angle setting a display of the trigger and event rates during the first 10 seconds will pop up. Also, after each angle the run will be closed, run summary information printed to the log, the stage rotated, a new data file opened, and a new run started. All of that takes a few seconds. (Capability for doing runs with continuous stage rotation is being worked on.)

When the scan is finished, click the “Quit” button to close the GUI. It is best to restart it from scratch for the next scan.

If the system will not be operated for an extended time period, use the power control GUI to turn off the tracker power and tracker bias. This will help keep the system from overheating and keep the bias currents from getting too high.

# Data Verification

It is a good idea at the beginning of a beam test to take an “empty” run with data reduction turned off in the energy detector FPGAs. That is done in the pct_config.yaml file according to the line

- energy_detector:
  - data_type: samples

Just be sure to set it back to “reduced” before making scans. To verify the basic instrument performance, run the single-event display program in the /home/daq/git/pct-acquire/ folder:

python display_events.py file-name

It will open a window and display the first event. To go to the next event just delete the window. Use ctrl-c to exit the program. Make sure that you see tracker hits forming reasonably straight lines and energy detector pulses for each stage in which the entire pulse fits into the 16 available samples. The pulse position can be adjusted with the “energy_detector: trigger_delay” parameter in pct_config.yaml.

It is also a good idea to take one or more reasonably long (millions of events) “empty” run with data reduction turned on. When the run is finished, execute the monitoring program to verify the data. In the /home/dat/git/pct-acquire/ folder execute the C++ program:

./DataMonitor file_name num_events

where the last argument (optional) is the number of events to analyze (you can analyze all the millions if you are patient, but set to 10000 for a quick look).

The monitoring program will create a bunch of .png files that you should then look at one by one. For each tracker cassette you should see strip hit maps that reflect the beam profile and, hopefully, don’t have many dead or noisy strips. For the energy detector you should see a single-proton peak, at least, for each layer plus more-or-less uniform T and V profiles. For the tracker you should see good T and V residuals plus efficiencies in the 99% -plus range.

# System Shut-Down

Use the power control GUI to power off the tracker bias and the tracker and energy detector supplies. Manually turn off the energy detector high voltage. Then power off the stage controller and the tracker and energy detector power supplies and bias voltages. Finally, turn off the event builder power.

pCT Phase-II ScannerPage 8

pCT Operating Instructions

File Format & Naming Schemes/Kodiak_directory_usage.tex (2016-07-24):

\Section{Kodiak Directory Descriptions and Usage}[Description of User/Shared Directories on Kodiak]
\begin{tcbenvironment}'tcbBlueStyle'[title=\shadowText{Kodiak}]
%%%%%%%%%%%%%%%%%%%%%%%%%%%%%%%%%%%%%%%%%%%%%%%%%%%%%%%%%%%%%%%%%%%%%%%%%%%%%%%%%%%%%%%%%%%%%%%%%%%%%%%%%%%%%%%%%%%%%%%%%%%%%%%%%%%%%%%%%%%%%
%%%%%%%%%%%%%%%%%%%%%%%%%%%%%%%%%%%%%%%%% /ion/... %%%%%%%%%%%%%%%%%%%%%%%%%%%%%%%%%%%%%%%%%%%%%%%
%%%%%%%%%%%%%%%%%%%%%%%%%%%%%%%%%%%%%%%%%%%%%%%%%%%%%%%%%%%%%%%%%%%%%%%%%%%%%%%%%%%%%%%%%%%%%%%%%%%%%%%%%%%%%%%%%%%%%%%%%%%%%%%%%%%%%%%%%%%%%
\begin{tcbparagraph}'tcbBlueStyle'(title=\dirsep ion\dirsep$\dots$)%<18.9cm><0.0cm>
	$\boldsymbol{-}$ This directory is dedicated to the storage of all files associated with proton and ion therapy research.  There are private and shared subdirectories and to prevent inappropriate modifications/deletions of shared code/data, users only have write permissions to their private directories and they cannot directly add/modify shared data.  To share data with the collaboration, users submit the data to their private ``staging'' directory using the appropriate naming/organization and an administrator will then validate the data and move it to the appropriate shared directory.  Administrators typically will not be familiar with the naming/organizational scheme, but by organizing the data according to the full destination path, administrators can move the entire hierarchy of files/folders directly to \docentry[constdir]{ion}, thereby merging the contents of any existing directories automatically.\\[\tcbparskip]
	
\indent\indent The data in this directory is located on a network storage device and can be accessed from all Kodiak and Tardis cluster nodes.  The device is also backed up to tape drive periodically to prevent permanent loss of data in the event of drive failure.
\end{tcbparagraph}
%%%%%%%%%%%%%%%%%%%%%%%%%%%%%%%%%%%%%%%%%%%%%%%%%%%%%%%%%%%%%%%%%%%%%%%%%%%%%%%%%%%%%%%%%%%%%%%%%%%%%%%%%%%%%%%%%%%%%%%%%%%%%%%%%%%%%%%%%%%%%
%%%%%%%%%%%%%%%%%%%%%%%%%%%%%%%%%%%%% ion/home/<username>/... %%%%%%%%%%%%%%%%%%%%%%%%%%%%%%%%%%%%%
%%%%%%%%%%%%%%%%%%%%%%%%%%%%%%%%%%%%%%%%%%%%%%%%%%%%%%%%%%%%%%%%%%%%%%%%%%%%%%%%%%%%%%%%%%%%%%%%%%%%%%%%%%%%%%%%%%%%%%%%%%%%%%%%%%%%%%%%%%%%%
\begin{tcbparagraph}'tcbBlueStyle'%
(title=\dirsep ion\dirsep home\dirsep\caratenclosed*{username}\dirsep$\dots$)
$\boldsymbol{-}$ This is a user's private home directory where the files associated with their account are stored (e.g., \docentry[file]{\texttt{.bash\_profile}}, \docentry[file]{\texttt{.bash\_history}}, etc.) and is the default login directory.  Each user only has access to their personal directory, but because it is on the network storage device, it can be accessed from each of the Kodiak/Tardis nodes. Now that the home directories have been moved to \docentry[constdir]{ion}, they no longer have a limited storage capacity, so users may run code and write the resulting output data/images to this directory.  Note that as a subdirectory of \docentry[constdir]{ion}, the data in this directory will automatically be backed up to tape drive so it is recoverable in case of data corruption or drive failure.
\end{tcbparagraph}
%%%%%%%%%%%%%%%%%%%%%%%%%%%%%%%%%%%%%%%%%%%%%%%%%%%%%%%%%%%%%%%%%%%%%%%%%%%%%%%%%%%%%%%%%%%%%%%%%%%%%%%%%%%%%%%%%%%%%%%%%%%%%%%%%%%%%%%%%%%%%%%%%%%%%%%%%%%%%%%%%%%%%%%%%%%%%%%%%%%%%%%%%%%%%%%%%%%%%%%%%%%%%%%%%%%%%%%%%%%%%%
%%%%%%%%%%%%%%%%%%%%%%%%%%%%%%%%%%%%%%%%%% /data/<username>/... %%%%%%%%%%%%%%%%%%%%%%%%%%%%%%%%%
%%%%%%%%%%%%%%%%%%%%%%%%%%%%%%%%%%%%%%%%%%%%%%%%%%%%%%%%%%%%%%%%%%%%%%%%%%%%%%%%%%%%%%%%%%%%%%%%%%%%%%%%%%%%%%%%%%%%%%%%%%%%%%%%%%%%%%%%%%%%%%%%%%%%%%%%%%%%%%%%%%%%%%%%%%%%%%%%%%%%%%%%%%%%%%%%%%%%%%%%%%%%%%%%%%%%%%%%%%%%%%
\begin{tcbparagraph}'tcbBlueStyle'(title=\dirsep data\dirsep\caratenclosed*{username}\dirsep$\dots$)
$\boldsymbol{-}$ These private data directories can be used as an alternative to \docentry[dir]{ion\dirsep home\dirsep\caratenclosed*{username}} for storing input data for code/program execution and as the destination for the resulting output data generated.  As subdirectories of \docentry[constdir]{ data}, the contents of these directories are backed up periodically, so these can also be used for long term data storage.
\end{tcbparagraph}
%%%%%%%%%%%%%%%%%%%%%%%%%%%%%%%%%%%%%%%%%%%%%%%%%%%%%%%%%%%%%%%%%%%%%%%%%%%%%%%%%%%%%%%%%%%%%%%%%%%%%%%%%%%%%%%%%%%%%%%%%%%%%%%%%%%%%%%%%%%%%%%%%%%%%%%%%%%%%%%%%%%%%%%%%%%%%%%%%%%%%%%%%%%%%%%%%%%%%%%%%%%%%%%%%%%%%%%%%%%%%%
%%%%%%%%%%%%%%%%%%%%%%%%%%%%%%%%%%%%% ion/incoming/<username> %%%%%%%%%%%%%%%%%%%%%%%%%%%%%%%%%%
%%%%%%%%%%%%%%%%%%%%%%%%%%%%%%%%%%%%%%%%%%%%%%%%%%%%%%%%%%%%%%%%%%%%%%%%%%%%%%%%%%%%%%%%%%%%%%%%%%%%%%%%%%%%%%%%%%%%%%%%%%%%%%%%%%%%%%%%%%%%%%%%%%%%%%%%%%%%%%%%%%%%%%%%%%%%%%%%%%%%%%%%%%%%%%%%%%%%%%%%%%%%%%%%%%%%%%%%%%%%%%
\begin{tcbparagraph}'tcbBlueStyle'(title=\dirsep ion\dirsep incoming\dirsep\caratenclosed*{username}\dirsep$\dots$)
$\boldsymbol{-}$ These private directories are used to upload data to the Baylor server prior to moving it to the intended destination.  When the uploaded data is intended to be shared with the collaboration, the directory should be used to rename and organize the data files according to the naming/organizational scheme before moving it to a user's private \docentry[constdir]{staging} directory, from which an administrator will validate and move the data to the appropriate shared directory.
\end{tcbparagraph}
%%%%%%%%%%%%%%%%%%%%%%%%%%%%%%%%%%%%%%%%%%%%%%%%%%%%%%%%%%%%%%%%%%%%%%%%%%%%%%%%%%%%%%%%%%%%%%%%%%%%%%%%%%%%%%%%%%%%%%%%%%%%%%%%%%%%%%%%%%%%%%%%%%%%%%%%%%%%%%%%%%%%%%%%%%%%%%%%%%%%%%%%%%%%%%%%%%%%%%%%%%%%%%%%%%%%%%%%%%%%%%
%%%%%%%%%%%%%%%%%%%%%%%%%%%%%%%%%%%%% ion/staging/<username> %%%%%%%%%%%%%%%%%%%%%%%%%%%%%%%%%%%%%
%%%%%%%%%%%%%%%%%%%%%%%%%%%%%%%%%%%%%%%%%%%%%%%%%%%%%%%%%%%%%%%%%%%%%%%%%%%%%%%%%%%%%%%%%%%%%%%%%%%%%%%%%%%%%%%%%%%%%%%%%%%%%%%%%%%%%%%%%%%%%%%%%%%%%%%%%%%%%%%%%%%%%%%%%%%%%%%%%%%%%%%%%%%%%%%%%%%%%%%%%%%%%%%%%%%%%%%%%%%%%%
\begin{tcbparagraph}'tcbBlueStyle'(title=\dirsep ion\dirsep staging\dirsep\caratenclosed*{username}\dirsep$\dots$)
$\boldsymbol{-}$ These directories are used to submit code/data for sharing with the collaboration.  Since administrators are typically unfamiliar with the naming/organizational scheme for shared data, users must first rename/organize the data as needed to create the entire hierarchy of directories corresponding to the full destination path, including all subdirectories below \docentry[constdir]{ion}.  Administrators need not know the destination path or understand the organization but can then simply move the entire hierarchy and the contents of existing directories such as \docentry[constdir]{ion} will automatically be merged and the new data/directories added.  To simplify the creation of these hierarchies and ensure consistency by removing manual naming/organization, bash scripts/functions have been developed to organize data and move it to a user's \docentry[constdir]{staging} directory by passing the requisite information as execution parameters (e.g., phantom, run date/\#/tag(s), etc.).\\[\tcbparskip]
\end{tcbparagraph}
%%%%%%%%%%%%%%%%%%%%%%%%%%%%%%%%%%%%%%%%%%%%%%%%%%%%%%%%%%%%%%%%%%%%%%%%%%%%%%%%%%%%%%%%%%%%%%%%%%%%%%%%%%%%%%%%%%%%%%%%%%%%%%%%%%%%%%%%%%%%%%%%%%%%%%%%%%%%%%%%%%%%%%%%%%%%%%%%%%%%%%%%%%%%%%%%%%%%%%%%%%%%%%%%%%%%%%%%%%%%%%
%%%%%%%%%%%%%%%%%%%%%%%%%%%%%%%%%%%%% ion/pCT_data/... %%%%%%%%%%%%%%%%%%%%%%%%%%%%%%%%%%%%%%%%%%
%%%%%%%%%%%%%%%%%%%%%%%%%%%%%%%%%%%%%%%%%%%%%%%%%%%%%%%%%%%%%%%%%%%%%%%%%%%%%%%%%%%%%%%%%%%%%%%%%%%%%%%%%%%%%%%%%%%%%%%%%%%%%%%%%%%%%%%%%%%%%%%%%%%%%%%%%%%%%%%%%%%%%%%%%%%%%%%%%%%%%%%%%%%%%%%%%%%%%%%%%%%%%%%%%%%%%%%%%%%%%%
\begin{tcbparagraph}'tcbBlueStyle'(title=\dirsep ion\dirsep pCT\_data\dirsep$\dots$)
$\boldsymbol{-}$ This directory is where the raw, preprocessed, projection, and reconstruction data/images are moved to make them available to the other pCT users.  Each type of data is stored in separate subdirectories and soft links to this data are created and organized in a directory hierarchy indicating their input/output data dependencies.  The directory/file naming and organizational scheme for each type of data and the soft links are outlined in the next section of this document.  Data/images should only be moved to this shared directory after having been verified as valid/accurate and having been organized appropriately.
\end{tcbparagraph}
%%%%%%%%%%%%%%%%%%%%%%%%%%%%%%%%%%%%%%%%%%%%%%%%%%%%%%%%%%%%%%%%%%%%%%%%%%%%%%%%%%%%%%%%%%%%%%%%%%%%%%%%%%%%%%%%%%%%%%%%%%%%%%%%%%%%%%%%%%%%%%%%%%%%%%%%%%%%%%%%%%%%%%%%%%%%%%%%%%%%%%%%%%%%%%%%%%%%%%%%%%%%%%%%%%%%%%%%%%%%%%
%%%%%%%%%%%%%%%%%%%%%%%%%%%%%%%%%%%%% ion/pCT_data/pCT_Documentation %%%%%%%%%%%%%%%%%%%%%%%%%%%
%%%%%%%%%%%%%%%%%%%%%%%%%%%%%%%%%%%%%%%%%%%%%%%%%%%%%%%%%%%%%%%%%%%%%%%%%%%%%%%%%%%%%%%%%%%%%%%%%%%%%%%%%%%%%%%%%%%%%%%%%%%%%%%%%%%%%%%%%%%%%%%%%%%%%%%%%%%%%%%%%%%%%%%%%%%%%%%%%%%%%%%%%%%%%%%%%%%%%%%%%%%%%%%%%%%%%%%%%%%%%%
\begin{tcbparagraph}'tcbBlueStyle'(title=\dirsep ion\dirsep pCT\_data\dirsep pCT\_Documentation\dirsep $\dots$)
$\boldsymbol{-}$ Documentation relevant to pCT is stored in this directory, such as descriptions of the data format, coordinate system, and phantoms and pCT related publications (including student theses/dissertations).  This is a GitHub managed local repository allowing everyone to \docentry![subcategory]{push} contributions to the repository and \docentry![subcategory]{pull} updates/additions from others into their own local clone ensuring everyone has access to the latest information.
\end{tcbparagraph}
%%%%%%%%%%%%%%%%%%%%%%%%%%%%%%%%%%%%%%%%%%%%%%%%%%%%%%%%%%%%%%%%%%%%%%%%%%%%%%%%%%%%%%%%%%%%%%%%%%%%%%%%%%%%%%%%%%%%%%%%%%%%%%%%%%%%%%%%%%%%%%%%%%%%%%%%%%%%%%%%%%%%%%%%%%%%%%%%%%%%%%%%%%%%%%%%%%%%%%%%%%%%%%%%%%%%%%%%%%%%%%
%%%%%%%%%%%%%%%%%%%%%%%%%%%%%%%%%%%%% ion/pCT_code/... %%%%%%%%%%%%%%%%%%%%%%%%%%%%%%%%%%%%%%%%%%%
%%%%%%%%%%%%%%%%%%%%%%%%%%%%%%%%%%%%%%%%%%%%%%%%%%%%%%%%%%%%%%%%%%%%%%%%%%%%%%%%%%%%%%%%%%%%%%%%%%%%%%%%%%%%%%%%%%%%%%%%%%%%%%%%%%%%%%%%%%%%%%%%%%%%%%%%%%%%%%%%%%%%%%%%%%%%%%%%%%%%%%%%%%%%%%%%%%%%%%%%%%%%%%%%%%%%%%%%%%%%%%
\begin{tcbparagraph}'tcbBlueStyle'(title=\dirsep ion\dirsep pCT\_code\dirsep $\dots$)
$\boldsymbol{-}$ This directory is used to store permanent and semi-permanent pCT source code, from data acquisition to image reconstruction and analysis of reconstructed images.  It contains clones of GitHub repositories as well as user's personal versions of programs they want to make available to other users (otherwise users should keep their code in their private directories) organized by program type (Preprocessing/Reconstruction/etc.) with subdirectories for each user.
\end{tcbparagraph}
%%%%%%%%%%%%%%%%%%%%%%%%%%%%%%%%%%%%%%%%%%%%%%%%%%%%%%%%%%%%%%%%%%%%%%%%%%%%%%%%%%%%%%%%%%%%%%%%%%%%%%%%%%%%%%%%%%%%%%%%%%%%%%%%%%%%%%%%%%%%%%%%%%%%%%%%%%%%%%%%%%%%%%%%%%%%%%%%%%%%%%%%%%%%%%%%%%%%%%%%%%%%%%%%%%%%%%%%%%%%%%
%%%%%%%%%%%%%%%%%%%% ion/pCT_code/git/<GitHub account>/<GitHub repo>/... %%%%%%%%%%%%%%%%%%%%%%%%%%
%%%%%%%%%%%%%%%%%%%%%%%%%%%%%%%%%%%%%%%%%%%%%%%%%%%%%%%%%%%%%%%%%%%%%%%%%%%%%%%%%%%%%%%%%%%%%%%%%%%%%%%%%%%%%%%%%%%%%%%%%%%%%%%%%%%%%%%%%%%%%%%%%%%%%%%%%%%%%%%%%%%%%%%%%%%%%%%%%%%%%%%%%%%%%%%%%%%%%%%%%%%%%%%%%%%%%%%%%%%%%%
\begin{tcbparagraph}'tcbBlueStyle'(title=\dirsep ion\dirsep pCT\_code\dirsep git\dirsep\caratenclosed*{GitHub account}\dirsep\caratenclosed*{GitHub repository}\dirsep $\dots$)
$\boldsymbol{-}$ This directory contains clones of the available pCT GitHub accounts and repositories, with parent directories for each GitHub account and subdirectories for each of their repositories.  Each program repository has a \docentry[gitbranch]{master} branch, which typically corresponds to the current release version (though there may also be a branch like \docentry[gitbranch]{release} used instead) and each of the program's developers will typically have their own branch which they can use to develop and test new ideas/features.  The group of developers of a program should decide amongst themselves what the process will be for approving merges with the \docentry[gitbranch]{master/release} branch and when to release a new version of the program, which may include the results of several separate merges.\\[\tcbparskip]

Users accessing the \docentry[gitbranch]{master/release} branch of these clones should execute \tcbinlinebashbox!{git pull --rebase} prior to using the code to ensure it is updated to its latest version.\\[\tcbparskip]

\textbf{\ul{NOTE}: This should not be done for other branches or the personal versions of code}.
\end{tcbparagraph}
%%%%%%%%%%%%%%%%%%%%%%%%%%%%%%%%%%%%%%%%%%%%%%%%%%%%%%%%%%%%%%%%%%%%%%%%%%%%%%%%%%%%%%%%%%%%%%%%%%%%%%%%%%%%%%%%%%%%%%%%%%%%%%%%%%%%%%%%%%%%%%%%%%%%%%%%%%%%%%%%%%%%%%%%%%%%%%%%%%%%%%%%%%%%%%%%%%%%%%%%%%%%%%%%%%%%%%%%%%%%%%
%%%%%%%%%%%%%%%% ion/pCT_code/<Preprocessing/Reconstruction>/<username>/... %%%%%%%%%%%%%%%%%%%%%%%
%%%%%%%%%%%%%%%%%%%%%%%%%%%%%%%%%%%%%%%%%%%%%%%%%%%%%%%%%%%%%%%%%%%%%%%%%%%%%%%%%%%%%%%%%%%%%%%%%%%%%%%%%%%%%%%%%%%%%%%%%%%%%%%%%%%%%%%%%%%%%%%%%%%%%%%%%%%%%%%%%%%%%%%%%%%%%%%%%%%%%%%%%%%%%%%%%%%%%%%%%%%%%%%%%%%%%%%%%%%%%%
\begin{tcbparagraph}'tcbBlueStyle'(title=\dirsep ion\dirsep pCT\_code\dirsep user\_code\dirsep\caratenclosed*{username}\dirsep$\dots$)
$\boldsymbol{-}$ Contains subdirectories for each pCT user where they can store and modify clones of the pCT program repositories and their personal code.
\end{tcbparagraph}
%%%%%%%%%%%%%%%%%%%%%%%%%%%%%%%%%%%%%%%%%%%%%%%%%%%%%%%%%%%%%%%%%%%%%%%%%%%%%%%%%%%%%%%%%%%%%%%%%%%%%%%%%%%%%%%%%%%%%%%%%%%%%%%%%%%%%%%%%%%%%%%%%%%%%%%%%%%%%%%%%%%%%%%%%%%%%%%%%%%%%%%%%%%%%%%%%%%%%%%%%%%%%%%%%%%%%%%%%%%%%%
%%%%%%%%%%%%%%%%%%%%%%%%%%%%%%%%%%%%%%%%%%%%%%%%%%%%%%%%%%%%%%%%%%%%%%%%%%%%%%%%%%%%%%%%%%%%%%%%%%%%%%%%%%%%%%%%%%%%%%%%%%%%%%%%%%%%%%%%%%%%%%%%%%%%%%%%%%%%%%%%%%%%%%%%%%%%%%%%%%%%%%%%%%%%%%%%%%%%%%%%%%%%%%%%%%%%%%%%%%%%%%
%%%%%%%%%%%%%%%%%%%%%%%%%%%%%%%%%%%%%%%%%%%%%%%%%%%%%%%%%%%%%%%%%%%%%%%%%%%%%%%%%%%%%%%%%%%%%%%%%%%%%%%%%%%%%%%%%%%%%%%%%%%%%%%%%%%%%%%%%%%%%%%%%%%%%%%%%%%%%%%%%%%%%%%%%%%%%%%%%%%%%%%%%%%%%%%%%%%%%%%%%%%%%%%%%%%%%%%%%%%%%%
\end{tcbenvironment}
%%%%%%%%%%%%%%%%%%%%%%%%%%%%%%%%%%%%%%%%%%%%%%%%%%%%%%%%%%%%%%%%%%%%%%%%%%%%%%%%%%%%%%%%%%%%%%%%%%%%%%%%%%%%%%%%%%%%%%%%%%%%%%%%%%%%%%%%%%%%%%%%%%%%%%%%%%%%%%%%%%%%%%%%%%%%%%%%%%%%%%%%%%%%%%%%%%%%%%%%%%%%%%%%%%%%%%%%%%%%%%
%%%%%%%%%%%%%%%%%%%%%%%%%%%%%%%%%%%%%%%%%%%%%%%%%%%%%%%%%%%%%%%%%%%%%%%%%%%%%%%%%%%%%%%%%%%%%%%%%%%%%%%%%%%%%%%%%%%%%%%%%%%%%%%%%%%%%%%%%%%%%%%%%%%%%%%%%%%%%%%%%%%%%%%%%%%%%%%%%%%%%%%%%%%%%%%%%%%%%%%%%%%%%%%%%%%%%%%%%%%%%%
%%%%%%%%%%%%%%%%%%%%%%%%%%%%%%%%%%%%%%%%%%%%%%%%%%%%%%%%%%%%%%%%%%%%%%%%%%%%%%%%%%%%%%%%%%%%%%%%%%%%%%%%%%%%%%%%%%%%%%%%%%%%%%%%%%%%%%%%%%%%%%%%%%%%%%%%%%%%%%%%%%%%%%%%%%%%%%%%%%%%%%%%%%%%%%%%%%%%%%%%%%%%%%%%%%%%%%%%%%%%%%
\endinput

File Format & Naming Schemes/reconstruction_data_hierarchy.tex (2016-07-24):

\clearpage%
\Subsection{Reconstruction Data Hierarchy}
%%%%%%%%%%%%%%%%%%%%%%%%%%%%%%%%%%%%%%%%%%%%%%%%%%%%%%%%%%%%%%%%%%%%%%%%%%%%%%%%%%%%%%%%%%%%%%%%%%%%%%%%%%%%%%%%%%%%%%%%%%%%%%%%%%%%%%%%%%%%%%%%%%%%%%%%%%%%%%%%%%%%%%%%%%%%%%%%%%%%%%%%%%%%%%%%%%%%%%%%%%%%%%%%%%%%%%%%%%%%%%
\begin{tcbenvironment}'tcbBlueStyle'[title=\shadowText{reconstruction\_data}]
%%%%%%%%%%%%%%%%%%%%%%%%%%%%%%%%%%%%%%%%%%%%%%%%%%%%%%%%%%%%%%%%%%%%%%%%%%%%%%%%%%%%%%%%%%%%%%%%%%%%%%%%%%%%%%%%%%%%%%%%%%%%%%%%%%%%%%%%%%%%%%%%%%%%%%%%%%%%%%%%%%%%%%%%%%%%%%%%%%%%%%%%%%%%%%%%%%%%%%%%%%%%%%%%%%%%%%%%%%%%%%
\begin{tcbparagraph}'tcbBlueStyle'(title=\dirsep ion\dirsep pCT\_data\dirsep reconstruction\_data)%[title=\dirsep ion\dirsep pCT\_data/reconstruction\_data\dirsep$\dots$]
$\boldsymbol{-}$ directory containing the default data/images generated during reconstruction.  Additional data files and images can optionally be written to disk as well and a full list of these is given in the \autohyperlink[type=Section]{Reconstruction File List} section.
\end{tcbparagraph}
%%%%%%%%%%%%%%%%%%%%%%%%%%%%%%%%%%%%%%%%%%%%%%%%%%%%%%%%%%%%%%%%%%%%%%%%%%%%%%%%%%%%%%%%%%%%%%%%%%%%%%%%%%%%%%%%%%%%%%%%%%%%%%%%%%%%%%%%%%%%%%%%%%%%%%%%%%%%%%%%%%%%%%%%%%%%%%%%%%%%%%%%%%%%%%%%%%%%%%%%%%%%%%%%%%%%%%%%%%%%%%
\begin{tcbparagraph}'tcbBlueStyle'{tcbenumeratedStyle}
    \begin{ThinEnum}
	  \item \docentry[file]{execution\_log.csv} : global execution log containing entries with scan/object information and the settings/parameters used in reconstruction for each reconstructions performed to date, with new row entries added each time the reconstruction program is executed.
	  \item \docentry[dir]{Phantom} : directory containing all of the experimental/simulated data and reconstructed images associated with this phantom/object.
        \begin{ThinEnum}
            \item \docentry[constdir]{Reference\_Images} : directory containing reference images (xCT, RSP, etc) relevant to analysis/comparison of the data/images for this object and data type.
            \item \docentry[constdir]{Experimental} : directory containing data and images generated from an experimental scan of the object.
            \begin{ThinEnum}
                \item \docentry[dir]{YY-MM-DD} : directory containing data and reconstructed images corresponding to the experimental scan of the object performed on this date.
                \begin{ThinEnum}
                    \item \docentry[dir]{XXXX[\_AAA]} : directory containing data and reconstructed images corresponding to the 4-digit run \# \docentry![subcategory]{XXXX}, potentially including \emph{``subcategory tag(s)''} of the form \docentry![subcategory]{\_AAA} such as  \docentry![subcategory]{\_Cont} specifying a continuous scan and/or phantom positioning tags such as inferior (\docentry![subcategory]{\_Inf}) or superior (\docentry![subcategory]{\_Sup}), top (\docentry![subcategory]{\_Top}) or bottom (\docentry![subcategory]{\_Bot}), etc.
                    \begin{ThinEnum}
                        \item \docentry[constdir]{Input} : directory containing raw data generated by scan of object from each gantry angle and transmitted by event builder.
                        \begin{ThinEnum}
                            \item \docentry[fileset]{raw\_xxx.bin} : binary files containing trigger/tracker/energy detector data from event builder associated with gantry angle \docentry![subcategory]{xxx} =\{\docentry![subcategory]{001}, \docentry![subcategory]{002}, \docentry![subcategory]{003}, $\cdots\}$.
                        \end{ThinEnum}
                        \item \docentry[constdir]{Output} : directory containing calibration and post processed data generated from analysis of raw data and used as input to image reconstruction.
                        \begin{ThinEnum}
                            \item \docentry[dir]{YY-MM-DD} : directory containing the post processed \docentry![fileset]{projection\_xxx.bin} data generated on this date and the reconstructions using this data.
                            \begin{ThinEnum}
                                \item \docentry[file]{readme.txt} : contains input raw data info, phantom name, and run date.
                    			\item \docentry[file]{TVcorr.txt} : contains TV corrected WEPL calibration curve coefficients.
						\item \docentry[file]{WcalibTemp.txt} : temporary file containing WEPL calibration curve coefficients.
                                	\item \docentry[file]{Wcalib.txt} : contains final WEPL calibration curve coefficients.
%%%%%%%%%%%%%%%%%%%%%%%%%%%%%%%%%%%%%%%%%%%%%%%%%%%%%%%%%%%%%%%%%%%%%%%%%%%%%%%%%%%%%%%%%%%%%%%%%%%%%%%%%%%%%%%%%%%%%%%%%%%%%%%%%%%%%%%%%%%%%%%%%%%%%%%%%%%%%%%%%%%%%%%%%%%%%%%%%%%%%%%%%%%%%%%%%%%%%%%%%%%%%%%%%%%%%%%%%%%%%%
\newpage
%%%%%%%%%%%%%%%%%%%%%%%%%%%%%%%%%%%%%%%%%%%%%%%%%%%%%%%%%%%%%%%%%%%%%%%%%%%%%%%%%%%%%%%%%%%%%%%%%%%%%%%%%%%%%%%%%%%%%%%%%%%%%%%%%%%%%%%%%%%%%%%%%%%%%%%%%%%%%%%%%%%%%%%%%%%%%%%%%%%%%%%%%%%%%%%%%%%%%%%%%%%%%%%%%%%%%%%%%%%%%%
                                	\item \docentry[fileset]{projection\_xxx.bin} : preprocessed data files containing tracker coordinates and WEPL data for gantry angle $\text{\docentry![subcategory]{xxx}} =\{\text{\docentry![subcategory]{001}}, \text{\docentry![subcategory]{002}}, \text{\docentry![subcategory]{003}}, \cdots\}$ used as input to image reconstruction.
						\item \docentry[constdir]{Reconstruction} : directory containing preprocessed data and reconstructed images generated using the \docentry![fileset]{projection\_xxx.bin} data along with reference images relevant to the object.
                                	\begin{ThinEnum}
                                    	\item \docentry[file]{settings.cfg} : configuration file containing key/value pairs specifying scan/phantom properties
                                    (phantom, run date/\#/tag(s), etc.) and default reconstruction settings/parameters.
                    				\item \docentry[dir]{YY-MM-DD} : directory containing the preprocessed data generated on this date and the reconstructed images generated from this data.
                                    \begin{ThinEnum}
                                        	\item \docentry[file]{execution\_log.txt} : execution times for various portions of preprocessing and/or reconstruction and total program execution time.
                                        	\item \docentry[file]{FBP.txt} : text image of filtered back projection (FBP) image with the \xyplane* of each slice stacked on each other.
                                        	\item \docentry[file]{FBP.png} : conversion of \docentry![file]{FBP.txt} to PNG image.
                                        	\item \docentry[file]{FBP\_med\_filtered.txt} : text image result of applying median filter to the filtered back projection (FBP) image with the \xyplane* of each slice stacked on each other.
                                        	\item \docentry[file]{FBP\_med\_filtered.png} : conversion of \docentry![file]{FBP\_avg\_filtered.txt} to PNG image.
                                        	\item \docentry[file]{hull.txt} : text image of selected object hull in 1s/0s with the \xyplane* of each slice stacked on each other.
                                        	\item \docentry[file]{hull.png} : conversion of \docentry![file]{hull.txt} to PNG image.
                                        	\item \docentry[file]{hull\_avg\_filtered.txt} : text image result of applying average filter to the hull image with the \xyplane* of each slice stacked on each other.
							\item \docentry[file]{hull\_avg\_filtered.png} : conversion of \docentry![file]{hull\_avg\_filtered.txt} to PNG image.
							\item \docentry[file]{settings\_log.cfg} : copy of \docentry![file]{settings.cfg} with any changes made to parameters/options applied at execution, if any.
                                        	\item \docentry[file]{TV\_measurements.txt} : contains total variation (TV) measurements before/after each iteration
                                        	\item \docentry[file]{x\_0.txt} : text image of initial iterate with the \xyplane* of each slice stacked on each other.
                                        \item \docentry[file]{x\_0.png} : conversion of \docentry![file]{x\_0.txt} to PNG image.
                                        \item \docentry[constdir]{Images} : directory containing reconstructed images generated using this preprocessed data.
                                        \begin{ThinEnum}
                                            \item \docentry[dir]{YY-MM-DD} : directory containing the reconstructed images generated on this date using the preprocessed data above.
                                                \begin{ThinEnum}
                                                    \item \docentry[fileset]{x\_k.txt} : text image of reconstructed image $\boldsymbol{x^k}$ after $\boldsymbol{k}$ iterations.
                                                    \item \docentry[fileset]{x\_k.png} : PNG image of reconstructed image $\boldsymbol{x^k}$ after $\boldsymbol{k}$ iterations.
                                                \end{ThinEnum}
                                        \end{ThinEnum}
                                    \end{ThinEnum}
                                \end{ThinEnum}
                            \end{ThinEnum}
                        \end{ThinEnum}
                    \end{ThinEnum}
                \end{ThinEnum}
            \end{ThinEnum}
            %\newpage
            \item \docentry[constdir]{Simulated} : directory containing data and images generated from simulated scans of the object.
            \begin{ThinEnum}
                \item \docentry[dir]{G\_YY-MM-DD} : directory containing data and reconstructed images from the GEANT4 simulated scan of the object generated on this date..
%%%%%%%%%%%%%%%%%%%%%%%%%%%%%%%%%%%%%%%%%%%%%%%%%%%%%%%%%%%%%%%%%%%%%%%%%%%%%%%%%%%%%%%%%%%%%%%%%%%%%%%%%%%%%%%%%%%%%%%%%%%%%%%%%%%%%%%%%%%%%%%%%%%%%%%%%%%%%%%%%%%%%%%%%%%%%%%%%%%%%%%%%%%%%%%%%%%%%%%%%%%%%%%%%%%%%%%%%%%%%%
\newpage
%%%%%%%%%%%%%%%%%%%%%%%%%%%%%%%%%%%%%%%%%%%%%%%%%%%%%%%%%%%%%%%%%%%%%%%%%%%%%%%%%%%%%%%%%%%%%%%%%%%%%%%%%%%%%%%%%%%%%%%%%%%%%%%%%%%%%%%%%%%%%%%%%%%%%%%%%%%%%%%%%%%%%%%%%%%%%%%%%%%%%%%%%%%%%%%%%%%%%%%%%%%%%%%%%%%%%%%%%%%%%%
                \begin{ThinEnum}
                    \item \docentry[dir]{XXXX[\_AAA]} : directory containing data and reconstructed images corresponding to the 4-digit run \# \docentry![subcategory]{XXXX}, potentially including \emph{``subcategory tag(s)''} of the form \docentry![subcategory]{\_AAA} such as  \docentry![subcategory]{\_Cont} specifying a continuous scan and/or phantom positioning tags such as inferior (\docentry![subcategory]{\_Inf}) or superior (\docentry![subcategory]{\_Sup}), top (\docentry![subcategory]{\_Top}) or bottom (\docentry![subcategory]{\_Bot}), etc.
                    \begin{ThinEnum}
                        \item \docentry[constdir]{Input} : directory containing raw data files generated by simulated scan of object for each gantry angle.
                        \begin{ThinEnum}
                            \item \docentry[fileset]{raw\_xxx.bin} : binary files containing trigger/tracker/energy detector data from event builder associated with gantry angle \docentry![subcategory]{xxx} =\{\docentry![subcategory]{001}, \docentry![subcategory]{002}, \docentry![subcategory]{003}, $\cdots\}$.
                        \end{ThinEnum}
                        \item \docentry[constdir]{Output} : directory containing calibration and post processed data generated from analysis of raw data and used as input to image reconstruction.
                        \begin{ThinEnum}
                            \item \docentry[dir]{YY-MM-DD} : directory containing the post processed \docentry![fileset]{projection\_xxx.bin} data generated on this date and the reconstructions using this data.
                            \begin{ThinEnum}
                                \item \docentry[file]{readme.txt} : contains input raw data info, phantom name, and run date.
                    			\item \docentry[file]{TVcorr.txt} : contains TV corrected WEPL calibration curve coefficients.
						\item \docentry[file]{WcalibTemp.txt} : temporary file containing WEPL calibration curve coefficients.
                                	\item \docentry[file]{Wcalib.txt} : contains final WEPL calibration curve coefficients.
                                \item \docentry[fileset]{projection\_xxx.bin} : preprocessed data files containing tracker coordinates and WEPL data for gantry angle $\text{\docentry![subcategory]{xxx}} =\{\text{\docentry![subcategory]{001}}, \text{\docentry![subcategory]{002}}, \text{\docentry![subcategory]{003}}, \cdots\}$ used as input to image reconstruction.                         	
                                \item \docentry[constdir]{Reconstruction} : directory containing preprocessed data and reconstructed images generated using the \docentry![fileset]{projection\_xxx.bin} data along with reference images relevant to the object.
                                	\begin{ThinEnum}
                                    	\item \docentry[file]{settings.cfg} : configuration file containing key/value pairs specifying scan/phantom properties
                                    (phantom, run date/\#/tag(s), etc.) and default reconstruction settings/parameters.
                    				\item \docentry[dir]{YY-MM-DD} : directory containing the preprocessed data generated on this date and the reconstructed images generated from this data.                    			
                    			\begin{ThinEnum}
                                        	\item \docentry[file]{execution\_log.txt} : execution times for various portions of preprocessing and/or reconstruction and total program execution time.
                                        	\item \docentry[file]{FBP.txt} : text image of filtered back projection (FBP) image with the \xyplane* of each slice stacked on each other.
                                        	\item \docentry[file]{FBP.png} : conversion of \docentry![file]{FBP.txt} to PNG image.
                                        	\item \docentry[file]{FBP\_med\_filtered.txt} : text image result of applying median filter to the filtered back projection (FBP) image with the \xyplane* of each slice stacked on each other.
                                        	\item \docentry[file]{FBP\_med\_filtered.png} : conversion of \docentry![file]{FBP\_avg\_filtered.txt} to PNG image.
                                        	\item \docentry[file]{hull.txt} : text image of selected object hull in 1s/0s with the \xyplane* of each slice stacked on each other.
                                        	\item \docentry[file]{hull.png} : conversion of \docentry![file]{hull.txt} to PNG image.
                                        	\item \docentry[file]{hull\_avg\_filtered.txt} : text image result of applying average filter to the hull image with the \xyplane* of each slice stacked on each other.
							\item \docentry[file]{hull\_avg\_filtered.png} : conversion of \docentry![file]{hull\_avg\_filtered.txt} to PNG image.
%%%%%%%%%%%%%%%%%%%%%%%%%%%%%%%%%%%%%%%%%%%%%%%%%%%%%%%%%%%%%%%%%%%%%%%%%%%%%%%%%%%%%%%%%%%%%%%%%%%%%%%%%%%%%%%%%%%%%%%%%%%%%%%%%%%%%%%%%%%%%%%%%%%%%%%%%%%%%%%%%%%%%%%%%%%%%%%%%%%%%%%%%%%%%%%%%%%%%%%%%%%%%%%%%%%%%%%%%%%%%%
\newpage
%%%%%%%%%%%%%%%%%%%%%%%%%%%%%%%%%%%%%%%%%%%%%%%%%%%%%%%%%%%%%%%%%%%%%%%%%%%%%%%%%%%%%%%%%%%%%%%%%%%%%%%%%%%%%%%%%%%%%%%%%%%%%%%%%%%%%%%%%%%%%%%%%%%%%%%%%%%%%%%%%%%%%%%%%%%%%%%%%%%%%%%%%%%%%%%%%%%%%%%%%%%%%%%%%%%%%%%%%%%%%%
							\item \docentry[file]{settings\_log.cfg} : copy of \docentry![file]{settings.cfg} with any changes made to parameters/options applied at execution, if any.
                                        	\item \docentry[file]{TV\_measurements.txt} : contains total variation (TV) measurements before/after each iteration
                                        	\item \docentry[file]{x\_0.txt} : text image of initial iterate with the \xyplane* of each slice stacked on each other.
                                        \item \docentry[file]{x\_0.png} : conversion of \docentry![file]{x\_0.txt} to PNG image.
                                        \item \docentry[constdir]{Images} : directory containing reconstructed images generated using this preprocessed data.
                                        \begin{ThinEnum}
                                            \item \docentry[dir]{YY-MM-DD} : directory containing the reconstructed images generated on this date using the preprocessed data above.
                                                \begin{ThinEnum}
                                                    \item \docentry[fileset]{x\_k.txt} : text image of reconstructed image $\boldsymbol{x^k}$ after $\boldsymbol{k}$ iterations.
                                                    \item \docentry[fileset]{x\_k.png} : PNG image of reconstructed image $\boldsymbol{x^k}$ after $\boldsymbol{k}$ iterations.
                                                \end{ThinEnum}
                                        \end{ThinEnum}
                                    \end{ThinEnum}
                                \end{ThinEnum}
                            \end{ThinEnum}
                        \end{ThinEnum}
                    \end{ThinEnum}
                \end{ThinEnum}
                \item \docentry[dir]{T\_YY-MM-DD} : directory containing data and reconstructed images corresponding to all TOPAS simulated scans of the object generated on this date.
                \begin{ThinEnum}
                    \item \docentry[dir]{XXXX[\_AAA]} : directory containing data and reconstructed images corresponding to the 4-digit run \# \docentry![subcategory]{XXXX}, potentially including \emph{``subcategory tag(s)''} of the form \docentry![subcategory]{\_AAA} such as  \docentry![subcategory]{\_Cont} specifying a continuous scan and/or phantom positioning tags such as inferior (\docentry![subcategory]{\_Inf}) or superior (\docentry![subcategory]{\_Sup}), top (\docentry![subcategory]{\_Top}) or bottom (\docentry![subcategory]{\_Bot}), etc.
                    \begin{ThinEnum}
                        \item \docentry[constdir]{Input} : directory containing raw data files generated by simulated scan of object for each gantry angle.
                        \begin{ThinEnum}
                            \item \docentry[fileset]{raw\_xxx.bin} : binary files containing trigger/tracker/energy detector data from event builder associated with gantry angle \docentry![subcategory]{xxx} =\{\docentry![subcategory]{001}, \docentry![subcategory]{002}, \docentry![subcategory]{003}, $\cdots\}$.
                        \end{ThinEnum}
                        \item \docentry[constdir]{Output} : directory containing calibration and post processed data generated from analysis of raw data and used as input to image reconstruction.
                        \begin{ThinEnum}
                            \item \docentry[dir]{YY-MM-DD} : directory containing the post processed \docentry![fileset]{projection\_xxx.bin} data generated on this date and the reconstructions using this data.
                            \begin{ThinEnum}
                                \item \docentry[file]{readme.txt} : contains input raw data info, phantom name, and run date.
                    			\item \docentry[file]{TVcorr.txt} : contains TV corrected WEPL calibration curve coefficients.
						\item \docentry[file]{WcalibTemp.txt} : temporary file containing WEPL calibration curve coefficients.
                                	\item \docentry[file]{Wcalib.txt} : contains final WEPL calibration curve coefficients.
                                \item \docentry[fileset]{projection\_xxx.bin} : preprocessed data files containing tracker coordinates and WEPL data for gantry angle $\text{\docentry![subcategory]{xxx}} =\{\text{\docentry![subcategory]{001}}, \text{\docentry![subcategory]{002}}, \text{\docentry![subcategory]{003}}, \cdots\}$ used as input to image reconstruction.                       	
                                \item \docentry[constdir]{Reconstruction} : directory containing preprocessed data and reconstructed images generated using the \docentry![fileset]{projection\_xxx.bin} data along with reference images relevant to the object.
                                	\begin{ThinEnum}
                                    	\item \docentry[file]{settings.cfg} : configuration file containing key/value pairs specifying scan/phantom properties
                                    (phantom, run date/\#/tag(s), etc.) and default reconstruction settings/parameters.
%%%%%%%%%%%%%%%%%%%%%%%%%%%%%%%%%%%%%%%%%%%%%%%%%%%%%%%%%%%%%%%%%%%%%%%%%%%%%%%%%%%%%%%%%%%%%%%%%%%%%%%%%%%%%%%%%%%%%%%%%%%%%%%%%%%%%%%%%%%%%%%%%%%%%%%%%%%%%%%%%%%%%%%%%%%%%%%%%%%%%%%%%%%%%%%%%%%%%%%%%%%%%%%%%%%%%%%%%%%%%%
\newpage
%%%%%%%%%%%%%%%%%%%%%%%%%%%%%%%%%%%%%%%%%%%%%%%%%%%%%%%%%%%%%%%%%%%%%%%%%%%%%%%%%%%%%%%%%%%%%%%%%%%%%%%%%%%%%%%%%%%%%%%%%%%%%%%%%%%%%%%%%%%%%%%%%%%%%%%%%%%%%%%%%%%%%%%%%%%%%%%%%%%%%%%%%%%%%%%%%%%%%%%%%%%%%%%%%%%%%%%%%%%%%%
                    				\item \docentry[dir]{YY-MM-DD} : directory containing the preprocessed data generated on this date and the reconstructed images generated from this data.
                                    \begin{ThinEnum}
                                        	\item \docentry[file]{execution\_log.txt} : execution times for various portions of preprocessing and/or reconstruction and total program execution time.
                                        	\item \docentry[file]{FBP.txt} : text image of filtered back projection (FBP) image with the \xyplane* of each slice stacked on each other.
                                        	\item \docentry[file]{FBP.png} : conversion of \docentry![file]{FBP.txt} to PNG image.
                                        	\item \docentry[file]{FBP\_med\_filtered.txt} : text image result of applying median filter to the filtered back projection (FBP) image with the \xyplane* of each slice stacked on each other.
                                        	\item \docentry[file]{FBP\_med\_filtered.png} : conversion of \docentry![file]{FBP\_avg\_filtered.txt} to PNG image.
                                        	\item \docentry[file]{hull.txt} : text image of selected object hull in 1s/0s with the \xyplane* of each slice stacked on each other.
                                        	\item \docentry[file]{hull.png} : conversion of \docentry![file]{hull.txt} to PNG image.
                                        	\item \docentry[file]{hull\_avg\_filtered.txt} : text image result of applying average filter to the hull image with the \xyplane* of each slice stacked on each other.
							\item \docentry[file]{hull\_avg\_filtered.png} : conversion of \docentry![file]{hull\_avg\_filtered.txt} to PNG image.
							\item \docentry[file]{settings\_log.cfg} : copy of \docentry![file]{settings.cfg} with any changes made to parameters/options applied at execution, if any.
                                        	\item \docentry[file]{TV\_measurements.txt} : contains total variation (TV) measurements before/after each iteration
                                        	\item \docentry[file]{x\_0.txt} : text image of initial iterate with the \xyplane* of each slice stacked on each other.
%%%%%%%%%%%%%%%%%%%%%%%%%%%%%%%%%%%%%%%%%%%%%%%%%%%%%%%%%%%%%%%%%%%%%%%%%%%%%%%%%%%%%%%%%%%%%%%%%%%%%%%%%%%%%%%%%%%%%%%%%%%%%%%%%%%%%%%%%%%%%%%%%%%%%%%%%%%%%%%%%%%%%%%%%%%%%%%%%%%%%%%%%%%%%%%%%%%%%%%%%%%%%%%%%%%%%%%%%%%%%%
\newpage
%%%%%%%%%%%%%%%%%%%%%%%%%%%%%%%%%%%%%%%%%%%%%%%%%%%%%%%%%%%%%%%%%%%%%%%%%%%%%%%%%%%%%%%%%%%%%%%%%%%%%%%%%%%%%%%%%%%%%%%%%%%%%%%%%%%%%%%%%%%%%%%%%%%%%%%%%%%%%%%%%%%%%%%%%%%%%%%%%%%%%%%%%%%%%%%%%%%%%%%%%%%%%%%%%%%%%%%%%%%%%%
                                        \item \docentry[file]{x\_0.png} : conversion of \docentry![file]{x\_0.txt} to PNG image.
                                        \item \docentry[constdir]{Images} : directory containing reconstructed images generated using this preprocessed data.
                                        \begin{ThinEnum}
                                            \item \docentry[dir]{YY-MM-DD} : directory containing the reconstructed images generated on this date using the preprocessed data above.
                                                \begin{ThinEnum}
                                                    \item \docentry[fileset]{x\_k.txt} : text image of reconstructed image $\boldsymbol{x^k}$ after $\boldsymbol{k}$ iterations.
                                                    \item \docentry[fileset]{x\_k.png} : PNG image of reconstructed image $\boldsymbol{x^k}$ after $\boldsymbol{k}$ iterations.
                                                \end{ThinEnum}
                                        \end{ThinEnum}
                                    \end{ThinEnum}
                                \end{ThinEnum}
                            \end{ThinEnum}
                        \end{ThinEnum}
                    \end{ThinEnum}
                \end{ThinEnum}
            \end{ThinEnum}
        \end{ThinEnum}
    \end{ThinEnum}
%%%%%%%%%%%%%%%%%%%%%%%%%%%%%%%%%%%%%%%%%%%%%%%%%%%%%%%%%%%%%%%%%%%%%%%%%%%%%%%%%%%%%%%%%%%%%%%%%%%%%%%%%%%%%%%%%%%%%%%%%%%%%%%%%%%%%%%%%%%%%%%%%%%%%%%%%%%%%%%%%%%%%%%%%%%%%%%%%%%%%%%%%%%%%%%%%%%%%%%%%%%%%%%%%%%%%%%%%%%%%%
\end{tcbparagraph}
%\par\bigskip\bigskip\bigskip\medskip
%%%%%%%%%%%%%%%%%%%%%%%%%%%%%%%%%%%%%%%%%%%%%%%%%%%%%%%%%%%%%%%%%%%%%%%%%%%%%%%%%%%%%%%%%%%%%%%%%%%%%%%%%%%%%%%%%%%%%%%%%%%%%%%%%%%%%%%%%%%%%%%%%%%%%%%%%%%%%%%%%%%%%%%%%%%%%%%%%%%%%%%%%%%%%%%%%%%%%%%%%%%%%%%%%%%%%%%%%%%%%%
\end{tcbenvironment}
%%%%%%%%%%%%%%%%%%%%%%%%%%%%%%%%%%%%%%%%%%%%%%%%%%%%%%%%%%%%%%%%%%%%%%%%%%%%%%%%%%%%%%%%%%%%%%%%%%%%%%%%%%%%%%%%%%%%%%%%%%%%%%%%%%%%%%%%%%%%%%%%%%%%%%%%%%%%%%%%%%%%%%%%%%%%%%%%%%%%%%%%%%%%%%%%%%%%%%%%%%%%%%%%%%%%%%%%%%%%%%
\endinput
%%%%%%%%%%%%%%%%%%%%%%%%%%%%%%%%%%%%%%%%%%%%%%%%%%%%%%%%%%%%%%%%%%%%%%%%%%%%%%%%%%%%%%%%%%%%%%%%%%%%%%%%%%%%%%%%%%%%%%%%%%%%%%%%%%%%%%%%%%%%%%%%%%%%%%%%%%%%%%%%%%%%%%%%%%%%%%%%%%%%%%%%%%%%%%%%%%%%%%%%%%%%%%%%%%%%%%%%%%%%%%
%%%%%%%%%%%%%%%%%%%%%%%%%%%%%%%%%%%%%%%%%%%%%%%%%%%%%%%%%%%%%%%%%%%%%%%%%%%%%%%%%%%%%%%%%%%%%%%%%%%%%%%%%%%%%%%%%%%%%%%%%%%%%%%%%%%%%%%%%%%%%%%%%%%%%%%%%%%%%%%%%%%%%%%%%%%%%%%%%%%%%%%%%%%%%%%%%%%%%%%%%%%%%%%%%%%%%%%%%%%%%%
%%%%%%%%%%%%%%%%%%%%%%%%%%%%%%%%%%%%%%%%%%%%%%%%%%%%%%%%%%%%%%%%%%%%%%%%%%%%%%%%%%%%%%%%%%%%%%%%%%%%%%%%%%%%%%%%%%%%%%%%%%%%%%%%%%%%%%%%%%%%%%%%%%%%%%%%%%%%%%%%%%%%%%%%%%%%%%%%%%%%%%%%%%%%%%%%%%%%%%%%%%%%%%%%%%%%%%%%%%%%%%
\item \docentry[file]{bin\_counts.txt} : linearized bin \# for each proton history, where linearized bin \# = t\_bin + angle\_bin * T\_BINS + v\_bin * T\_BINS * ANGULAR\_BINS.
\item {\docentry[file]{mean\_rel\_ut\_angle.txt} : mean relative ut angle ($\angle ut_{out} -\angle ut_{in}$) by linearized bin \#.}
\item \docentry[file]{mean\_rel\_uv\_angle.txt} : mean relative uv angle ($\angle uv_{out} -\angle uv_{in}$) by linearized bin \#.
\item \docentry[file]{mean\_WEPL.txt} : mean WEPL value by linearized bin \#.
\item \docentry[file]{stddev\_rel\_ut\_angle.txt} : standard deviation of the relative ut angle ($\angle ut_{out} -\angle ut_{in}$) by linearized bin \#.
\item \docentry[file]{stddev\_rel\_uv\_angle.txt} : standard deviation of the relative uv angle ($\angle uv_{out} -\angle uv_{in}$) by linearized bin \#.
\item \docentry[file]{stddev\_WEPL.txt} : standard deviation of the WEPL value by linearized bin \#.
\item \docentry[file]{sinogram.txt} : mean WEPL after statistical cuts with the $t_{bin}$ and angular bin $\theta_{bin}$ plane for each vertical bin $v_{bin}$ stacked on each other.
\item \docentry[file]{sin\_table.bin} : file containing the tabulated values of sine function
\item \docentry[file]{cos\_table.bin} : file containing the tabulated values of cosine function
\item \docentry[file]{coefficient.bin} : file containing the tabulated scattering coefficient values for $\Sigma_1$/$\Sigma_2$ for $u_2-u_1$/$u_1$ values
\item \docentry[file]{poly\_1\_2.bin} : file containing the tabulated MLP polynomial values with coefficients $\{1,2,3,4,5,6\}$
\item \docentry[file]{poly\_2\_3.bin} : file containing the tabulated MLP polynomial values with coefficients $\{2,3,4,5,6,7\}$
\item \docentry[file]{poly\_3\_4.bin} : file containing the tabulated MLP polynomial values with coefficients $\{3,4,5,6,7,8\}$
\item \docentry[file]{poly\_2\_6.bin} : file containing the tabulated MLP polynomial values with coefficients $\{2,6,12,20,30,42\}$
\item \docentry[file]{poly\_3\_12.bin} : file containing the tabulated MLP polynomial values with coefficients $\{3,12,30,60,105,168\}$
\item \docentry[file]{MLP.bin} : binary file with MLP path data for each history entering hull.
\item \docentry[file]{WEPL.bin} : binary file specifying WEPL value for each history entering hull.
\item \docentry[file]{histories.bin} : binary file specifying entry/exit coordinates/angles, bin number, gantry angle, and hull entry x/y/z voxel \# for each history entering hull.

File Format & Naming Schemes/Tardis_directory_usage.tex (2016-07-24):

\clearpage%
\Section{Tardis Compute Node Directory Descriptions and Usage}[Description of User/Shared Directories on Tardis Compute Nodes]
\begin{tcbenvironment}'tcbBlueStyle'[title=\shadowText{Tardis}]%
%%%%%%%%%%%%%%%%%%%%%%%%%%%%%%%%%%%%%%%%%%%%%%%%%%%%%%%%%%%%%%%%%%%%%%%%%%%%%%%%%%%%%%%%%%%%%%%%%%%%%%%%%%%%%%%%%%%%%%%%%%%%%%%%%%%%%%%%%%%%%
%%%%%%%%%%%%%%%%%%%%%%%%%%%%%%%%%%%%%%%%% /ion/... %%%%%%%%%%%%%%%%%%%%%%%%%%%%%%%%%%%%%%%%%%%%%%%
%%%%%%%%%%%%%%%%%%%%%%%%%%%%%%%%%%%%%%%%%%%%%%%%%%%%%%%%%%%%%%%%%%%%%%%%%%%%%%%%%%%%%%%%%%%%%%%%%%%%%%%%%%%%%%%%%%%%%%%%%%%%%%%%%%%%%%%%%%%%%
\begin{tcbparagraph}'tcbBlueStyle'(title=\dirsep local\dirsep$\dots$)%
	$\boldsymbol{-}$ This directory is the parent directory for all pCT code/data on each Tardis compute node, the equivalent of the \docentry[constdir]{ion} directory on Kodiak.  This data is stored on the compute nodes' local solid-state drive and is not backed up, so users must ensure they copy data to Kodiak if they want to store it permanently
\end{tcbparagraph}
%%%%%%%%%%%%%%%%%%%%%%%%%%%%%%%%%%%%%%%%%%%%%%%%%%%%%%%%%%%%%%%%%%%%%%%%%%%%%%%%%%%%%%%%%%%%%%%%%%%%%%%%%%%%%%%%%%%%%%%%%%%%%%%%%%%%%%%%%%%%%%%%%%%%%%%%%%%%%%%%%%%%%%%%%%%%%%%%%%%%%%%%%%%%%%%%%%%%%%%%%%%%%%%%%%%%%%%%%%%%%%
%%%%%%%%%%%%%%%%%%%%%%%%%%%%%%%%%%%%% ion/pCT_code/... %%%%%%%%%%%%%%%%%%%%%%%%%%%%%%%%%%%%%%%%%%%
%%%%%%%%%%%%%%%%%%%%%%%%%%%%%%%%%%%%%%%%%%%%%%%%%%%%%%%%%%%%%%%%%%%%%%%%%%%%%%%%%%%%%%%%%%%%%%%%%%%%%%%%%%%%%%%%%%%%%%%%%%%%%%%%%%%%%%%%%%%%%%%%%%%%%%%%%%%%%%%%%%%%%%%%%%%%%%%%%%%%%%%%%%%%%%%%%%%%%%%%%%%%%%%%%%%%%%%%%%%%%%
\begin{tcbparagraph}'tcbBlueStyle'(title=\dirsep local\dirsep pCT\_code\dirsep $\dots$)
$\boldsymbol{-}$ This directory is used to store pCT code on the Tardis compute nodes and corresponds to the \docentry[constdir]{ion\dirsep pCT\_code} directory on Kodiak (with the same organizatioal scheme as well).
\end{tcbparagraph}
%%%%%%%%%%%%%%%%%%%%%%%%%%%%%%%%%%%%%%%%%%%%%%%%%%%%%%%%%%%%%%%%%%%%%%%%%%%%%%%%%%%%%%%%%%%%%%%%%%%%%%%%%%%%%%%%%%%%%%%%%%%%%%%%%%%%%%%%%%%%%%%%%%%%%%%%%%%%%%%%%%%%%%%%%%%%%%%%%%%%%%%%%%%%%%%%%%%%%%%%%%%%%%%%%%%%%%%%%%%%%%
%%%%%%%%%%%%%%%% ion/pCT_code/<Preprocessing/Reconstruction>/<username>/... %%%%%%%%%%%%%%%%%%%%%%%
%%%%%%%%%%%%%%%%%%%%%%%%%%%%%%%%%%%%%%%%%%%%%%%%%%%%%%%%%%%%%%%%%%%%%%%%%%%%%%%%%%%%%%%%%%%%%%%%%%%%%%%%%%%%%%%%%%%%%%%%%%%%%%%%%%%%%%%%%%%%%%%%%%%%%%%%%%%%%%%%%%%%%%%%%%%%%%%%%%%%%%%%%%%%%%%%%%%%%%%%%%%%%%%%%%%%%%%%%%%%%%
\begin{tcbparagraph}'tcbBlueStyle'(title=\dirsep local\dirsep pCT\_code\dirsep user\_code\dirsep\caratenclosed*{username}\dirsep$\dots$)
$\boldsymbol{-}$ The equivalent of Kodiak's \docentry[constdir]{ion\dirsep pCT\_code\dirsep user\_code\dirsep\caratenclosed*{username}\dirsep$\dots$} subdirectories where pCT users can copy/modify/execute their personal clones of pCT program repositories and their personal code on Tardis compute nodes
\end{tcbparagraph}
%%%%%%%%%%%%%%%%%%%%%%%%%%%%%%%%%%%%%%%%%%%%%%%%%%%%%%%%%%%%%%%%%%%%%%%%%%%%%%%%%%%%%%%%%%%%%%%%%%%%%%%%%%%%%%%%%%%%%%%%%%%%%%%%%%%%%%%%%%%%%%%%%%%%%%%%%%%%%%%%%%%%%%%%%%%%%%%%%%%%%%%%%%%%%%%%%%%%%%%%%%%%%%%%%%%%%%%%%%%%%%
%%%%%%%%%%%%%%%%%%%% ion/pCT_code/git/<GitHub account>/<GitHub repo>/... %%%%%%%%%%%%%%%%%%%%%%%%%%
%%%%%%%%%%%%%%%%%%%%%%%%%%%%%%%%%%%%%%%%%%%%%%%%%%%%%%%%%%%%%%%%%%%%%%%%%%%%%%%%%%%%%%%%%%%%%%%%%%%%%%%%%%%%%%%%%%%%%%%%%%%%%%%%%%%%%%%%%%%%%%%%%%%%%%%%%%%%%%%%%%%%%%%%%%%%%%%%%%%%%%%%%%%%%%%%%%%%%%%%%%%%%%%%%%%%%%%%%%%%%%
\begin{tcbparagraph}'tcbBlueStyle'(title=\dirsep local\dirsep pCT\_code\dirsep git\dirsep\caratenclosed*{GitHub account}\dirsep\caratenclosed*{GitHub repository}\dirsep $\dots$)
$\boldsymbol{-}$ This directory contains clones of the available pCT GitHub accounts and repositories, with parent directories for each GitHub account and subdirectories for each of their repositories.  Each program repository has a \docentry[gitbranch]{master} branch, which typically corresponds to the current release version (though there may also be a branch like \docentry[gitbranch]{release} used instead) and each of the program's developers will typically have their own branch which they can use to develop and test new ideas/features.  The group of developers of a program should decide amongst themselves what the process will be for approving merges with the \docentry[gitbranch]{master/release} branch and when to release a new version of the program, which may include the results of several separate merges.\\\par

Users accessing the \docentry[gitbranch]{master/release} branch of these clones should execute \tcbinlinebashbox!{git pull --rebase} prior to using the code to ensure it is updated to its latest version.  \textbf{\ul{NOTE}: This should not be done for other branches or the personal versions of code}.
\end{tcbparagraph}
%%%%%%%%%%%%%%%%%%%%%%%%%%%%%%%%%%%%%%%%%%%%%%%%%%%%%%%%%%%%%%%%%%%%%%%%%%%%%%%%%%%%%%%%%%%%%%%%%%%%%%%%%%%%%%%%%%%%%%%%%%%%%%%%%%%%%%%%%%%%%%%%%%%%%%%%%%%%%%%%%%%%%%%%%%%%%%%%%%%%%%%%%%%%%%%%%%%%%%%%%%%%%%%%%%%%%%%%%%%%%%
%%%%%%%%%%%%%%%%%%%%%%%%%%%%%%%%%%%%% ion/pCT_data/... %%%%%%%%%%%%%%%%%%%%%%%%%%%%%%%%%%%%%%%%%%
%%%%%%%%%%%%%%%%%%%%%%%%%%%%%%%%%%%%%%%%%%%%%%%%%%%%%%%%%%%%%%%%%%%%%%%%%%%%%%%%%%%%%%%%%%%%%%%%%%%%%%%%%%%%%%%%%%%%%%%%%%%%%%%%%%%%%%%%%%%%%%%%%%%%%%%%%%%%%%%%%%%%%%%%%%%%%%%%%%%%%%%%%%%%%%%%%%%%%%%%%%%%%%%%%%%%%%%%%%%%%%
\begin{tcbparagraph}'tcbBlueStyle'(title=\dirsep local\dirsep pCT\_data\dirsep$\dots$)
$\boldsymbol{-}$ This directory is where pCT data is to be copied from Kodiak and corresponds to the \docentry[constdir]{ion\dirsep pCT\_data} directory on Kodiak.
\end{tcbparagraph}
%%%%%%%%%%%%%%%%%%%%%%%%%%%%%%%%%%%%%%%%%%%%%%%%%%%%%%%%%%%%%%%%%%%%%%%%%%%%%%%%%%%%%%%%%%%%%%%%%%%%%%%%%%%%%%%%%%%%%%%%%%%%%%%%%%%%%%%%%%%%%%%%%%%%%%%%%%%%%%%%%%%%%%%%%%%%%%%%%%%%%%%%%%%%%%%%%%%%%%%%%%%%%%%%%%%%%%%%%%%%%%
%%%%%%%%%%%%%%%%%%%%%%%%%%%%%%%%%%%%% ion/pCT_data/... %%%%%%%%%%%%%%%%%%%%%%%%%%%%%%%%%%%%%%%%%%
%%%%%%%%%%%%%%%%%%%%%%%%%%%%%%%%%%%%%%%%%%%%%%%%%%%%%%%%%%%%%%%%%%%%%%%%%%%%%%%%%%%%%%%%%%%%%%%%%%%%%%%%%%%%%%%%%%%%%%%%%%%%%%%%%%%%%%%%%%%%%%%%%%%%%%%%%%%%%%%%%%%%%%%%%%%%%%%%%%%%%%%%%%%%%%%%%%%%%%%%%%%%%%%%%%%%%%%%%%%%%%
\begin{tcbparagraph}'tcbBlueStyle'(title=\dirsep local\dirsep pCT\_data\dirsep user\_data\dirsep\caratenclosed*{username}\dirsep$\dots$)
$\boldsymbol{-}$ Subdirectories for each pCT user on each Tardis compute node where they can transfer data they want to reconstruct when the data is not organized according to the pCT data naming/organizational scheme.  If the output data they generate will also be unorganized, it should also be written to this directory.\\\par

\textbf{\ul{NOTE}: The \docentry[gitrepo]{pCT-collaboration/pCT\_Tools} repository contains a script which loads a number of bash functions useful to pCT users, including a function that can be used to organize and then copy unorganized data to the organized data directory on the Tardis compute nodes}
\end{tcbparagraph}
%%%%%%%%%%%%%%%%%%%%%%%%%%%%%%%%%%%%%%%%%%%%%%%%%%%%%%%%%%%%%%%%%%%%%%%%%%%%%%%%%%%%%%%%%%%%%%%%%%%%%%%%%%%%%%%%%%%%%%%%%%%%%%%%%%%%%%%%%%%%%%%%%%%%%%%%%%%%%%%%%%%%%%%%%%%%%%%%%%%%%%%%%%%%%%%%%%%%%%%%%%%%%%%%%%%%%%%%%%%%%%
%%%%%%%%%%%%%%%%%%%%%%%%%%%%%%%%%%%%%%%%%%%%%%%%%%%%%%%%%%%%%%%%%%%%%%%%%%%%%%%%%%%%%%%%%%%%%%%%%%%%%%%%%%%%%%%%%%%%%%%%%%%%%%%%%%%%%%%%%%%%%%%%%%%%%%%%%%%%%%%%%%%%%%%%%%%%%%%%%%%%%%%%%%%%%%%%%%%%%%%%%%%%%%%%%%%%%%%%%%%%%%
%%%%%%%%%%%%%%%%%%%%%%%%%%%%%%%%%%%%%%%%%%%%%%%%%%%%%%%%%%%%%%%%%%%%%%%%%%%%%%%%%%%%%%%%%%%%%%%%%%%%%%%%%%%%%%%%%%%%%%%%%%%%%%%%%%%%%%%%%%%%%%%%%%%%%%%%%%%%%%%%%%%%%%%%%%%%%%%%%%%%%%%%%%%%%%%%%%%%%%%%%%%%%%%%%%%%%%%%%%%%%%
\end{tcbenvironment}
%%%%%%%%%%%%%%%%%%%%%%%%%%%%%%%%%%%%%%%%%%%%%%%%%%%%%%%%%%%%%%%%%%%%%%%%%%%%%%%%%%%%%%%%%%%%%%%%%%%%%%%%%%%%%%%%%%%%%%%%%%%%%%%%%%%%%%%%%%%%%%%%%%%%%%%%%%%%%%%%%%%%%%%%%%%%%%%%%%%%%%%%%%%%%%%%%%%%%%%%%%%%%%%%%%%%%%%%%%%%%%
%%%%%%%%%%%%%%%%%%%%%%%%%%%%%%%%%%%%%%%%%%%%%%%%%%%%%%%%%%%%%%%%%%%%%%%%%%%%%%%%%%%%%%%%%%%%%%%%%%%%%%%%%%%%%%%%%%%%%%%%%%%%%%%%%%%%%%%%%%%%%%%%%%%%%%%%%%%%%%%%%%%%%%%%%%%%%%%%%%%%%%%%%%%%%%%%%%%%%%%%%%%%%%%%%%%%%%%%%%%%%%
%%%%%%%%%%%%%%%%%%%%%%%%%%%%%%%%%%%%%%%%%%%%%%%%%%%%%%%%%%%%%%%%%%%%%%%%%%%%%%%%%%%%%%%%%%%%%%%%%%%%%%%%%%%%%%%%%%%%%%%%%%%%%%%%%%%%%%%%%%%%%%%%%%%%%%%%%%%%%%%%%%%%%%%%%%%%%%%%%%%%%%%%%%%%%%%%%%%%%%%%%%%%%%%%%%%%%%%%%%%%%%
\endinput

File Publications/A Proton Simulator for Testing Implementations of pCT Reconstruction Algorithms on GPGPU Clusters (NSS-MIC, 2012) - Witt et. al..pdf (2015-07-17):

2012 IEEE Nuclear Science Symposiwn and Medical Imaging Conference Record (NSS/MIC) | HT-4-1

# A Proton Simulator for Testing Implementations of Proton CT Reconstruction Algorithms on GPGPU Clusters

Micah Witt[l], Blake Schultze[l], Reinhard Schulte[2],[3] IEEE Member, Keith Schubert[1],[3] IEEE Sr. Member, and Ernesto Gomez[l] IEEE Member

Abstract-Proton computed tomography (pCT) is an image modality that will improve treatment planning for patients receiving proton radiation therapy compared with the current treatment techniques, which are based on X-ray CT. Reconstruction of a pCT image requires solving a large and sparse system of linear equations, which should be accomplished within a few minutes in order to be clinically practical. Analyzing the efficiency of potentially clinical reconstruction implementations requires multiple quality pCT data sets. The purpose of this paper is to describe the simulator that was developed to generate realistic pCT data sets to be used in testing the efficiency of reconstruction algorithms, in particular string-averaging and block-iterative projection algorithms using sparse matrix formats on General Purpose Graphics Processing Units (GPGPU)s.

I. INTRODUCTION
P

ROTON computed tomography (pCT) is an imaging modality that tracks protons as they traverse objects to be imaged. In proton radiation therapy, pCT imaging will provide improved treatment planning compared with the current method of X-ray CT imaging, because pCT will provide more accurate range prediction. Accurate range prediction is important, for example, for sparing critical normal structures. A pCT image is reconstructed by solving a very large system of linear equations of approximately 100 million equations with 10 million variables for a head-size object, in which the solution provides the relative stopping power (RSP) of every partition (voxel) of the object. In order to solve such a system in a reasonable time frame so that pCT can be practical for clinical use, a parallel projection algorithm must be implemented across a mUlti-processor computing system. Analyzing the convergence as well as the time and memory complexity of the reconstruction algorithms requires multiple high-quality data sets. Generating real data in the laboratory by using the proton beam on a physical phantom is expensive and time-consuming. Due to its highly technical nature, using the

Manuscript received November 16, 2012. This work was supported by the National Institute of Health and the National Science Foundation under Grant No. lROlEB013118·01 The content is solely the responsibility of the authors and does not necessarily represent the official views of the National Institute Of Biomedical Imaging And Bioengineering or the National Institutes of Health.
[llSchool of Computer Science and Engineering, California State University San Bernardino, San Bernardino CA 92407 USA, email: micah@r2Iabs.org.
[21Department of Radiation Medicine, Loma Linda University Medical Center, Loma Linda CA 92354 USA, email: rschulte@dominion.Uumc.edu. [31Department of Basic Sciences, Loma Linda University Medical Center, Loma Linda CA 92354 USA.

high energy physics simulation tool GEANT4 [6] to generate data sets is complex [2]. Therefore, a simulator that can quickly generate high-quality data sets will be essential in developing a clinically practical reconstruction methodology. Furthermore, it will be advantageous to add several parameter options to assist in analyzing other reconstruction issues such as noise and path prediction.
This paper describes the simulator that has been developed to generate realistic data to be used in testing the efficiency of parallel reconstruction implementations on GPUs for pCT imaging.

II. METHODS
A pCT simulator was developed to provide pCT data sets for solving the system of linear equations

Ax =b

where the A-matrix contains the proton path information, the b-vector contains the water equivalent path length (WEPL) of individual protons [7], and the x-vector represents the unknown RSP values of each voxel. The simulator stores the actual-solution-vector for a given phantom. The simulator creates a large user-determined number of realistic proton paths and corresponding elements of the matrix A, as well as the measurement vector b of WEPL values with or without added noise. The simulator can be operated in 2D or 3D mode providing the option of generating smaller 2D data sets along with realistically sized 3D data sets.

A. Phantoms
The simulator developed in this work uses a general class of phantoms inspired by Herman's digital head phantom [1] called a non-homogenious ellipse object (NEO) that allows for the addition of different RSP regions to represent different anatomical features.
In this work two NEO phantom versions, NEO 1 and NEO 2 shown in Figure 1 (a) and (b) respectively, were used to generate simulation examples. Both phantoms are bounded by an outer ellipse with major and minor axis length of 180 mm and 140 mm, respectively, and have inner regions representing the cerebral ventricles filled with cerebro-spinal fluid (RSP of 0.9), brain tissue (RSP of 1.04), an air-filled frontal sinus (RSP of 0.0), and compact skull bone (RSP of 1.6). NEO 2 also includes an outer skin layer.
978-1-4673-2030-6/12/$31.00 ©20 12 IEEE | 4329

(a) (b)

Fig. 1. Non-homogenious Ellipse Objects (NEOs): (a) NEO 1, (b) NEO 2.

The simulator allows for different size voxels and reconstruction volume in 3D mode, or pixels and reconstruction area in 2D mode. The 2D simulation examples used 1 mm x 1 Illin pixels and a reconstruction area of 200 mm x 160 mm, consistent with the cross-sectional size of an adult human head, resulting in 32,000 pixels. The simulator has three options for selecting the RSP for pixels along the elliptical boundaries containing two different RSP values. The center-point method selects the RSP at the center of each pixel. The corner-point averaging method uses the average of the RSP at the four corners of the pixel providing a smoother transition between different RSP regions than the center-point method. The weighted-area average method provides the smoothest transition between two different RSP regions by setting the boundary pixel values to the sum of each region's RSP times the fraction of its area with respect to the pixel area. The simulation examples used the corner-point averaging method. The simulator can also create 3D phantoms by stacking a user-defined number of slices with user-defined height of 2D phantoms, which results in an elliptical cylinder. Stacking 200 Imm-slices of the phantom for example results in an elliptical cylinder within a reconstruction volume of 200x200x160 = 6.4 million voxels, where each voxel is 1 mm3
| , creating data
volumes consistent with the clinical setting of a human head.
B. Proton Paths
The simulator projects parallel, linear proton paths from a virtual point source at infinite distance into the reconstruction space and then into the phantom. The entry points into the reconstruction volume are uniformly distributed over a userselected interval along the horizontal t-axis of the beam-specific coordinate sytem (2) for the 2D simulation and along the horizontal axis and vetical v-axis for the 3D simulation. In the simulation examples, were uniformly distributed over the interval [-125 mm, 125 mm] along the t-axis.
Once the entry point into the phantom is determined, the exit point is calculated by projecting a straight-line path with the addition of a lateral and angular displacement to model multiple Coulomb scattering (MCS). Given the entry and exit points, the actual proton path connects the two points and then, outside the phantom, the path continues in a straight-line. The simulator allows for either straight-line or cubic-spline paths.

proton
origination

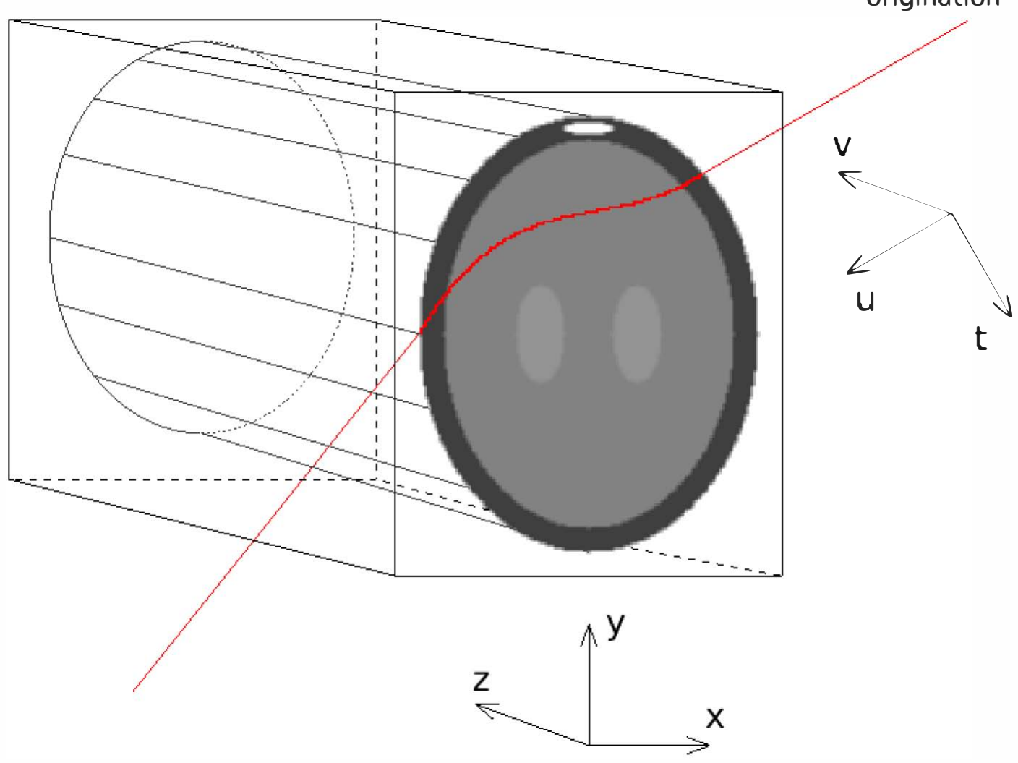
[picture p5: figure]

Fig. 2. Proton simulator geometry. A randomly generated proton path passing through the dIgItal phantom m the reconstruction space is shown. The t, v, u axes are the beam·specific coordinate system and the x, y, z axes are the coord mates of the global reconstruction space.

The simulation examples used straight-line paths.
Proton paths are directed from a user-specified number of projection angles with a user-defined angular spacing interval. The simulation examples used 180 projection angles with 2-degree spacing intervals, covering a full circle with a series of parallel 2D beams. For each projection, the proton paths are generated in the ut-plane of the beam-specific coordinate system.
The random variables describing lateral and angular displacement at the proton exit are approximately distributed according to a bivariate normal distribution described by Highland's formalism of MCS [4] with constants recommended by the Particle Data Group [5]. For the 2D mode of this simulator a bivariate normal distribution is used to generate rando number pairs to represent the exiting lateral displacement and angular deviation due to MCS of the proton within the phantom. For the 3D mode, the random exit parameters are calculated for the horiozontal ut-plane and the vertical uvplane separately since the lateral and vertical MCS of a proton are independent statistical processes.
For the bivariate normal distribution, let the two random variables be X and Y, then the probability density function is

## f(x,y)

where

1 | ( 1

exp ----
27r(Jx(Jyy(1 - p2) | 2(1 - p2)
[(X - f..L | x)² + (y - f..L | y)²
(J2 | (J2 x | y
_ 2p(x - f..L | x)(Y - f..L | y)]) , (J x(J y

p

vXY corr(X, Y) = -,

vXY | cov(X, Y),
[f..L | xf..L | y]

## (Jxy

The simulator has its own bivariate normal random number generator (BNRNG). The BNRNG begins with two uniform random variables generated using the randO function in the C standard library. It then converts those two uniform random variables to two standard independent random normals using the Marsaglia Polar-Method (modification of Box-Muller Method). The two independent normals are then converted into a pair of bivariate normals using the covariance matrix.

C. Mathematical Formulation of the Reconstruction Problem The elements of a given row of the A-matrix are the chord lengths of a given path through the pixels/voxels it intersected. In the simulator, the element ai
,

j is the chord length of the i

t
h
path through the lh pixel/voxel. For simplicity, the simulation examples used a constant chord length of the pixel size (1 mm).

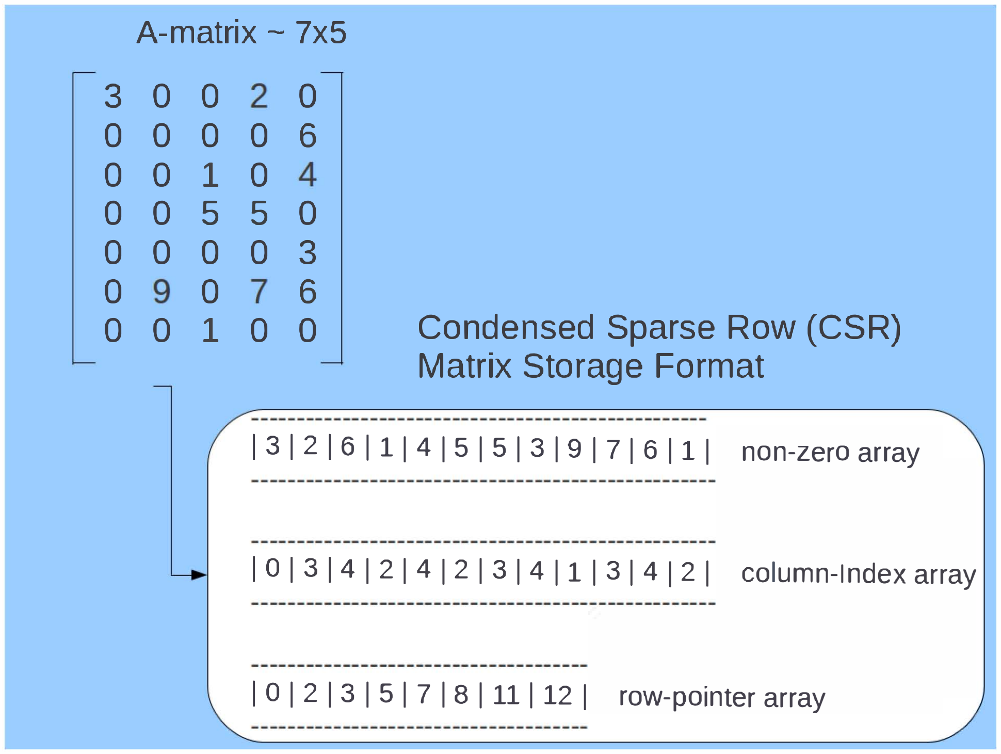
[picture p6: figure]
A-matrix - 7x5 0 0 2 0 0 0 0 6 0 1 0 4 0 5 5 0 0 0 0 3 9 0 7 6; Condensed Sparse Row (CSR); Matrix Storage Format

I 3 I 2 I 6 11 I 4 I 5 I 5 I 3 I 9 I 7 I 6 11 I non-zero array

101314 I 2 I 4 12 I 3 14 111 314 12 I column-Index array

I 0 I 2 I 3 I 5 I 7 I 8 111 112 I row-pointer array

The path of the proton is generated in the tvu-coordinate Fig. 3. An example of converting a dense matrix to condensed sparse row
system and then mapped to the stationary xyz-coordinate format.
system using a Givens rotational matrix. The simulator then
takes the xyz location of the path and intersects the path with
the voxels of the reconstruction space. Each proton path will intersect very few of the voxels in the entire reconstruction space so the vast majority of the entries in each row will be zero. To identify every voxel intersected by a proton path, the simulator uses the Digital Difference Analyzer method [1]. The noiseless WEPL value of the i

t
h proton is calculated
forming the inner product of the i

t
h row with the actualsolution-vector of the phantom. The simulator also has a feature that enables WEPL noise. To do this, the noiseless WEPL value is converted into an equivalent energy value of the exiting proton using the NIST PSTAR database [12]. Next, a random energy value is drawn from a normal distribution with mean equal to the noiseless energy and a standard deviation calculated using Tschalar's theory [11]. This noisy energy value is then converted into the noisy WEPL.
The number of voxels of the reconstruction volume defines the number of columns in the A-matrix. A reconstruction volume of 200 mm x 160 mm x 200 mm bounds the typical adult human head. A 3D simulation with a reconstruction volume of 6.4 million voxels and 64 million proton histories creates the system Ax = b with A E JR64Mx6.4M,

bE JR64M.
The simulator writes the A-matrix to a file in a format that can be easily read into condensed sparse row (CSR) matrix format [3] taking approximately 100 GB of disk space (Figure 3). Storing the A-matrix in dense form would require over 1 peta-byte of disk space (l peta = 1015). The data generated from a 2D simulation follows the same format.
D. Reconstruction Algorithm and Hardware
The string averaging projection (SAP) algorithm [10] was used in all reconstructions in this work. SAP allows matrix row partitions called strings to be calculated in parallel. The SAP algorithm is as follows:
Given the current iterate X

k E JRn
, calculate \It E
{I, 2, ... , M}, set yO xk and calculate, for 0,1, ... , m(t) - 1,

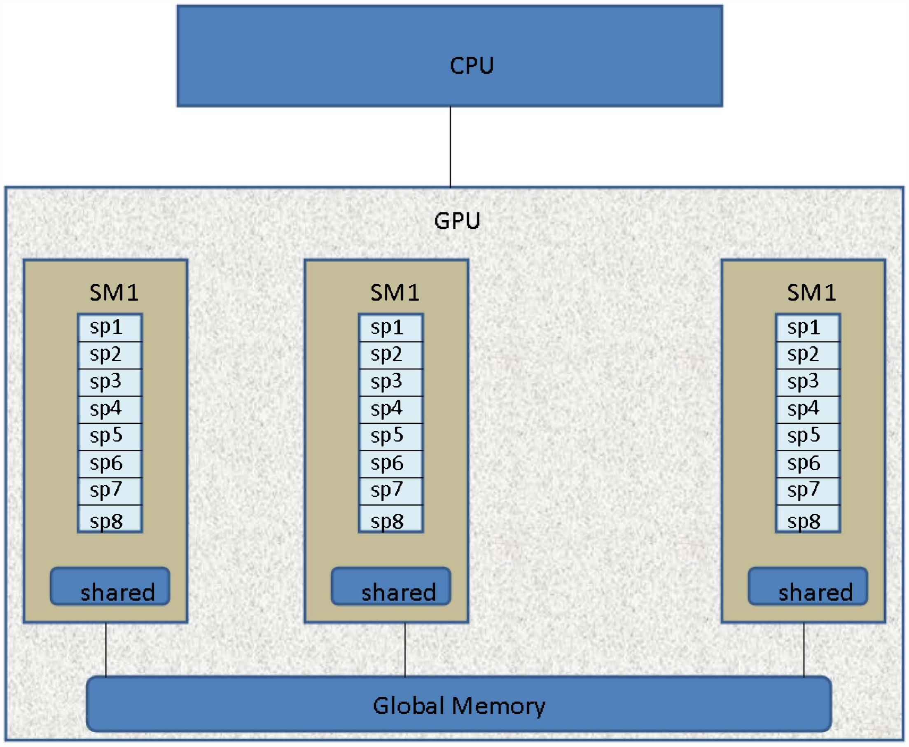
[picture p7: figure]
GPU; SMl; SMl sp1 sp2 sp3 sp4 sp5 sp6 sp7 s 8

Fig. 4. GPU architecture: SM-symmetric mUlti-processor, SP-stream processor, mem-memory. The GTX 280 has 30 SMs, with 8 SPs per SM for a total of 240 SPs, 1 GB of global memory, 16 KB of shared memory, 1.3 GHz clock speed.

and let y

t = y

m(t) for each t = 1,2, ... , M. Then calculate the next iterate by

M

## xk+1 = L Wty

t
)
t=l

where for the weight vectors w, Ll Wt = 1. The reconstructions of the simulation examples were performed with M = 100 string partitions.
The SAP reconstruction algorithm was performed on a GTX 280 with 240 stream processors, 1GB global memory (Figure 4).

(a) (b)
(c) (d)

Fig. 5. Reconstructions (n = 200 x 160 pixels) of the NEO 1 and NEO 2 phantoms (A = 0.1). (a) NEO 1 phantom, (b) reconstruction of NEO phantom, (c) NEO 2 phantom, (d) reconstruction of NEO 2 phantom.

III. RESULTS

Figures 5 through 7 show examples of reconstructions obtained without added WEPL noise. All reconstructions were performed with 20 iterations of the SAP algorithm. Figure 5 illustrates the 2D reconstruction of two slightly different head phantoms, NEO 1 and NEO 2. The reconstructions clearly show the different anatomical regions, characterized by different RSP values, for both phantom reconstructions.
Figure 6 analyzes the dependence of the image quality on the number of proton histories entering the reconstruction area, expressed as multiples of the number of pixels (32,000 pixels). The resulting images show decreasing image noise with increasing number of histories. The reason for the image noise, which is present despite the noiseless WEPL values, is the use of constant chord lengths in the reconstruction. Obviously the noise introduced by inaccurate chord lengths can be compensated by a larger number of proton histories. Figure 7 demonstrated the effects of different relaxation parameters on image quality with the same number of 20 iterations. There is a decrease of image noise with an increase in A, however, the effect of increasing A on noise reduction appears to saturate between A = 0.2 and A = 0.5.
Figures 8 and 9 demonstrate the effects of different numbers of histories and relaxation parameters on the quantitative accuracy of RSP values using line profiles through the two ventricles of the NEO 1 phantom. Given a sufficient number of histories and choice of an adequate relaxation parameter, accurate reconstruction of the RSP values was obtained.
(a) (b)
(c) (d)

Fig. 6. Reconstruction of the NEO 1 phantom with different number of histories m, expressed as multiples of the number of pixels n ( A = 0.1). (a)
m = n, (b) m = 5n, (c) m = lOn, (d) m = 20n.
(a) (b)
(c) (d)

Fig. 7. Reconstructions of the NEO 1 phantom using different relaxation
parameters A. (a) A = 0.01, (b) A = 0.1, (c) A = 0.2, (d) A = 0.5.

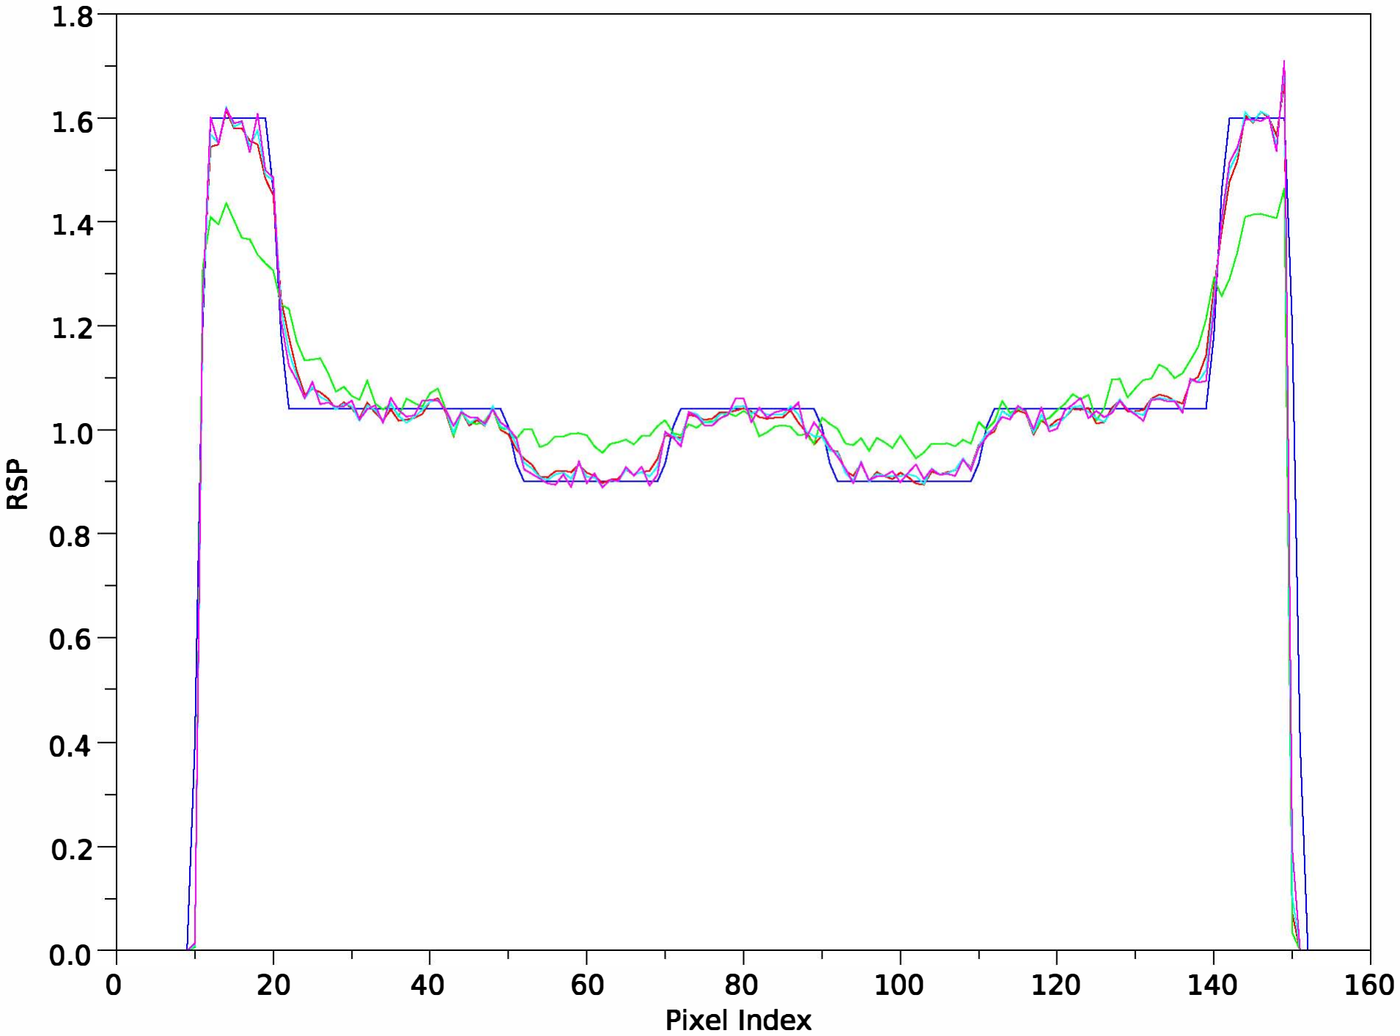
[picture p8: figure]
Pixel Index

Fig. 8. Line profiles through the ventricles of the NEO 1 phantom for different relaxation parameters A: NEO 1 (blue), A = 0.01 (green), A = 0.1 (red), A = 0.2 (cyan), A = 0.5 (magenta).

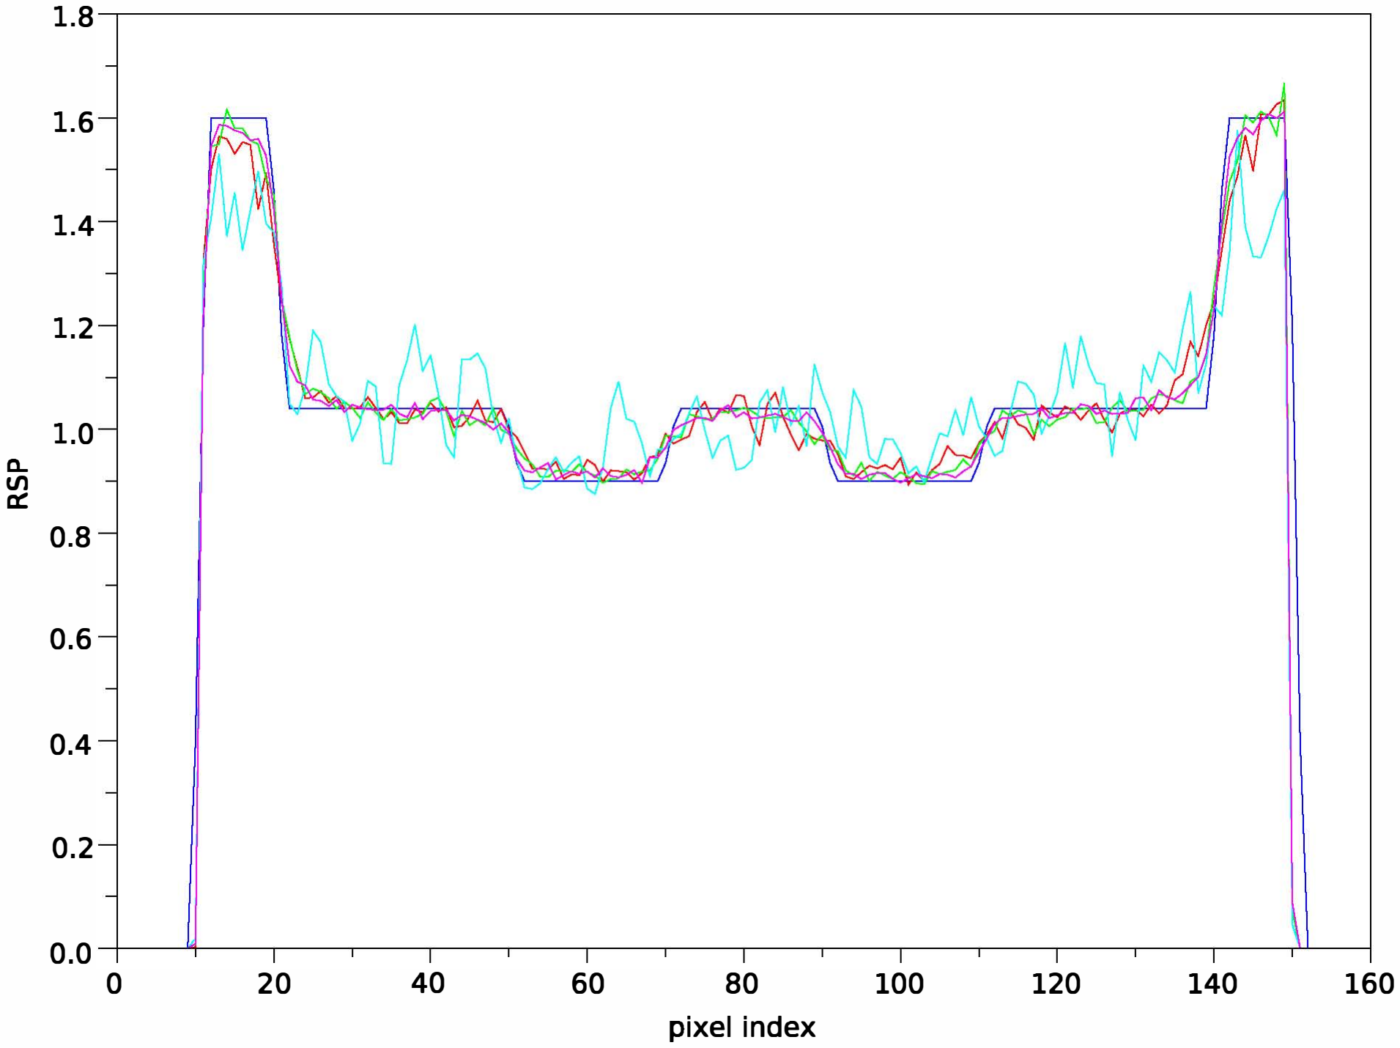
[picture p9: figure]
pixel Index

Fig. 9. Line profiles through the ventricles of the NEO 1 phantom using different numbers of histories: NEO 1 (blue), m = n (cyan), m = 5n (red), m = IOn (green), m = 20n (magenta).

IV. SUMMARY AND FUTURE DIRECTIONS

Fine-tuning and optimizing parameters of pCT reconstruction for the different varieties of pCT data that will be inherent in the actual application of this imaging modality requires a rapid turn-around of pCT reconstructions with realistic data sets. The simulator presented in this work allows for pCT data sets to be created through a variety of options using a realistic head phantoms and transport parameters for protons. It models a clinical setting in which virtual proton beams are directed from multiple angles simulating a 360-degree virtual proton gantry. Other features of the simulator, such as the ability to add noise or to use different path options with different accuracy, will be beneficial in systematically analyzing error

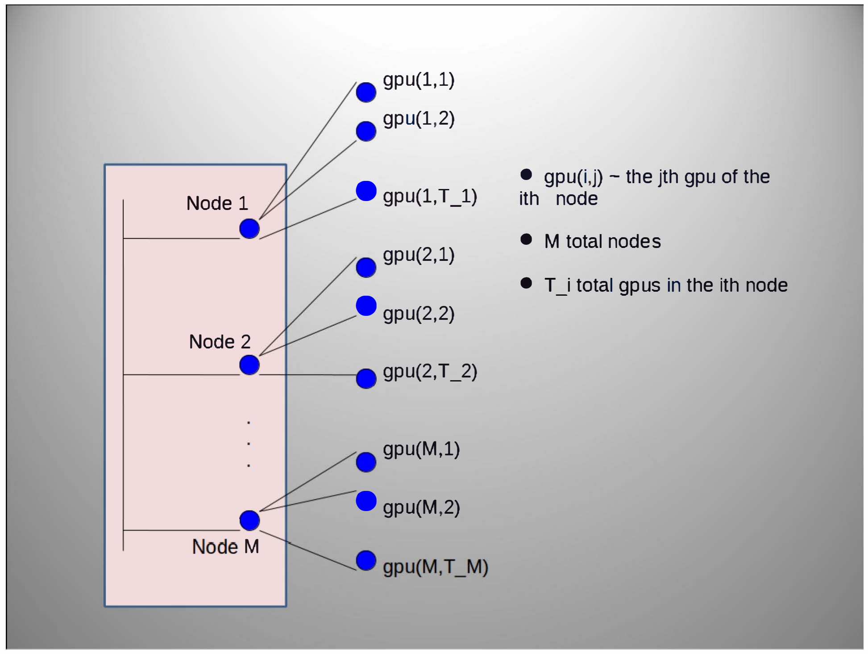
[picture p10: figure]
Node 1; Node 2; e gpu(l,l); e gpu(1,2); e gpu(l,T _1); e gpu(2,1); e gpu(2,2); gpu(2,T _2); e gpu(M,l); egpU(M,2); • gpu(i,j) - tile jth gpu of the Uh node; • M total nodes; • T _i total 9PuS in the ith node

Fig. 10. Conceptual design of a GPU cluster with M nodes. Each node has Ti GPUs, i=I,2, ...• M.

sources of pCT reconstruction.
The data sets produced by the simulator are written to disk memory in a format that can be read into data structures that will later be used in the implementation of existing and novel parallel projection algorithms across GPGPU clusters. Figure 10 shows the conceptual design of a typical GPGPU cluster as a collection of nodes, with each node comprised of multiple GPUs.
One of the major goals of this work is to develop an A-matrix partitioning scheme that will assign these partitions to nodes within a cluster and to GPUs within a node matching the structure inherent in the spatial and temporal acquisition scheme of the pCT system and the physical nature of the data to the internal architecture of the GPGPU cluster efficiently, i.e., rendering as many GPUs active as possible and minimizing the need of data transfer between different nodes. Figure 11 illustrates a general assignment scheme of matrix partitions to GPUs in a GPGPU cluster. The expected outcome of this research is a GPU-based reconstruction scheme that optimizes pCT reconstruction with respect to image quality, reconstruction time, and hardware expenses.
The pCT simulator, including source code and documentation, will be made readily available for researchers (physicists and engineers) as well as clinical physicists involved in proton therapy. At this point, all simulation code has been written in C++, the graphics package utilizes the OpenGL libraries, and all data analysis code has been written in C++, MatLab, and SciLab.

REFERENCES

[1] G. Herman, Fundamentals of Computerized Tomography,
2009.

Springer,

[2] S. Penfold. Image Reconstruction and Monte Carlo Simulations in the Development of Proton Computed Tomography for Applications in Proton
Radiation Therapy. Doctoral Thesis. University of Wollongong. Australia. 2010.
[3] N. Bell and M, Garland, Efficient Sparse Matrix-Vector Multitplication
on CUDA. NVIDIA Technical Report NVR-2008-004. December 2008.
[4] VL. Highland. "Some practical remarks on multiple scattering", Nuclear Instruments and Methods. vol. 129, pp. 497-499, 1975.

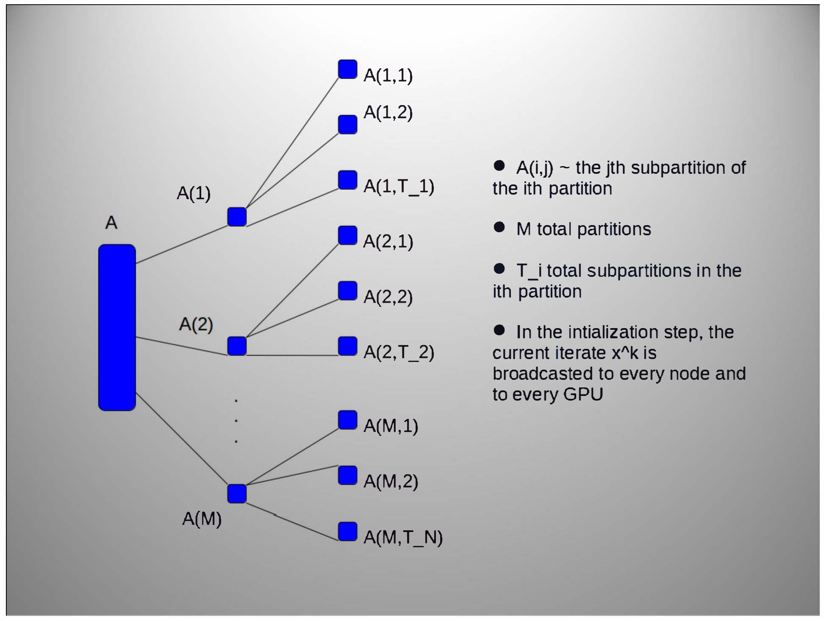
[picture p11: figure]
• A(i,j) - the jth subpart it ion of; the ith partition; • M total partitions A(2.1); • T J total 5ubpartitions in the; ith partition; • In the intialization step, the; current iterate x"k is; broadcasted to every node and to every GPU

Fig. 11. General concept of matrix parititioning and assignment to GPUs in a GPGPU cluster.

[5] K. Nakamura, et al. (Particle Data Group). "Review of Particle Physics,
27.3. Multiple scattering through small angles", 1. Phys., vol. G 37, pp. 290-291, 2010.
[6] S. Agostinelli, et aI., "GEANT4-A simulation toolkit", Nuclear Instru-
ments and Methods in Physics Research A, vol. 506, pp. 250-303, 2003.
[7] R. E Hurley, R. W Schulte, Y. A. Bashkirov, A. J. Wroe, A. Ghebremedhin, H. E-W Sadrozinski, Y. Rykalin and G. Coutrakon, P. Koss, B. Patyal, "Water-equivalent path length calibration of a prototype proton CT scanner," Med. Phys. vol. 39, pp. 2438-2246, 2012.
[8] R.W Schulte, S.N. Penfold, J.T. Tafas, and K.E. Schubert, "A maximum likelihood proton path formalism for application in proton computed tomography", Medical Physics, vol. 35, pp. 4849-4856, 2008.
[9] S.N. Penfold, R.W Schulte, K.E. Schubert, A.B. Rosenfeld, "A more accurate reconstruction system matrix for quantitative proton computed tomography", Medical Physics, vol. 36, pp. 4511-4518, 2009.
[10] Y. Censor, T. Elfving, and G.T. Hernam, "Averaging strings of sequential iterations for convex feasibilty problems," Inherently Parallel
Algorithms in Feasibility and Optimization and their Applications, Esevier
Science Publications, Amsterdam, The Netherlands, D. Butnnariu, Y. Censor, and S. Reich (Ed), 10 1-114 (2001).
[11] C. Tschalar, "Straggling distributions of extremely large energy losses,"
Nuclear Instruments and Methods, 61, 141-156 (1968).
[I2] NIST, National Institute of Standards and Technology PSTAR Database Program, http://physics.nist.gov/PhysRefDataiStar/Text/PSTAR.html.

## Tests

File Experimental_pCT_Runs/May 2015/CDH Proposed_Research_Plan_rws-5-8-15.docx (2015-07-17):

# Performance Evaluation of the Phase II Proton CT Scanner at CDH – Research Plan

# May – August, 2015

Background: In 2011 the NIH/NIBIB awarded us a 4-year R01 grant to build a fast preclinical head proton CT scanner and develop methods to reconstruct the data from a head object in 10 minutes or less. With the funding provided by that grant, we have built the phase II pCT scanner, which performs as promised. Another important task within the funded R01 project was to evaluate the clinically relevant imaging performance of the pCT scanner. Whereas the original application had stated we would do this with the phase I pCT scanner, which was the predecessor of the phase II scanner, we later decided to wait with this task until the new scanner was built and technically characterized and optimized.

We are now in the position to carry out the required tests to evaluate the clinical performance of the phase II pCT scanner at the Chicago Proton Center located at the Central DuPage Hospital (CDH) (http://www.chicagoprotoncenter.com/). This document details the research plan for the planned beam runs and data analysis.

Research Plan: The underlying hypothesis of our research is that pCT outperforms the current proton treatment planning and image guidance practice with a-high quality x-ray CT scan that is based on a stoichiometric conversion of CT Hounsfield units to relative proton stopping power (RSP) for treatment planning and a kV-cone beam CT for position and plan verification in the treatment room. The research plan outlined below aims at testing this hypothesis by performing an extensive performance evaluation of proton CT at CDH and compare the results to the standard approach with x-ray CT-based planning and cone-beam-CT based verification/image guidance in the treatment room.

Rationale of Research Approach: It is logical to test the pCT against a standard x-ray CT treatment planning scanner (CT simulator). Minimization of current proton range errors in the presence of tissue inhomogeneties is paramount for accurate proton treatment planning, and acceptable image quality at comparable doses is important for adequate target delineation and registration with other imaging modalities. Thus, we will focus on these two aspects of pCT imaging.

Approach: Three performance evaluation tasks will be completed utilizing the phase II prototype pCT system, a state-of-the-art multi-row detector CT scanner dedicated to proton treatment planning. The tests will be done at the CDH Proton Treatment Center in Warrenville, IL, which is a modern proton treatment facility with beam scanning capability and actively spread-out proton beams.

Task 1: Evaluate pCT image quality with phantoms and compare with x-ray CT image quality.

We will closely follow the guidelines of AAPM Task Force 2 outlined in AAPM Report No. 39, Specification and Acceptance Testing of Computed Tomography Scanners [1]. This task will evaluate

- Image noise (custom-built16-cm-diameter cylindrical water phantom)
- Field uniformity (custom-built16-cm-diameter cylindrical water phantom)
- High-contrast spatial frequency limits (Catphan, CTP528, high-resolution module)
- Modulation transfer function (MTF) (Custom-designed CIRS edge phantom)
- Low contrast detectability (Catphan, CTP515 low contrast module)
- Quantitative accuracy of RSP/CTN numbers (Catphan, CPT404 sensitometry phantom)
- Quantitative accuracy of RSP/CTN

Task 2: Evaluate pCT radiation dose and compare with x-ray CT dose obtained at the same image noise level.

We will closely follow the guidelines of the AAPM Report 111 of the Task Group #111: The Future of CT Dosimetry [2]. This task will evaluate the dose on the central axis and the surface of a 16 cm diameter cylindrical dose PMMA phantom. For both pCT and x-ray CT, the phantom will be exposed to uniform beam profiles of 80 mm length. The x-ray CT scan will be performed with nT = 64 x 1.25 mm and a field of view of 20 cm and using standard imaging parameters for a head scan otherwise. The pCT scan will be performed with an 8 cm x 20 cm field of 200 MeV protons and with 180 stationary projections at 2-deg increments. The total number of proton histories will be adjusted such that the central image noise of both scanning modalities will be identical to within +/-2.5%. The dose delivered by x-ray CT and pCT will be measured using a conventional thimble ionization chamber calibrated to 70-120 kV x-rays and with the chamber calibrated to measure proton doses in the 40-200 MeV energy range.

Task 3: Evaluate uncertainty of proton range determined with pCT and x-ray CT

The final test will be to evaluate the improved range estimation of pCT over conventional x-ray CT in proton therapy. To complete this, an anatomically detailed head phantom containing human tissue-equivalent soft tissue, brain, trabecular and compact bone, and sinus-air material (lung-equivalent) will be scanned with both imaging modalities using the setting of Task 2 that gives equivalent dose at the center of the phantom (to be verified by Geant4 Monte Carlo simulation). The water equivalent range of a pre-determined set of circular proton pencil beams (2 cm diameter) will be predicted for both planning modalities using a standard proton treatment planning system as well as by the TOPAS Monte Carlo simulation package. The head phantom contains a dosimetry insert in the posterior fossa that contains a stack of radiochromic film, which will allow us to measure the actual range of the delivered proton pencil beams to within better than +/- 0.1 mm.

Timeline: Three beam tests, further detailed below will be scheduled at the CDH proton facility during the months of May and June, 2015. The first run will take place on May 16, 2015.

# Detailed Plan for the CDH Beam Test on May 16, 2015

Phantoms (Abbrev.)

- Calibration Phantom (Calib/0) mounted on platform
- 4 additional polystyrene plates (100 x 400 x 50.8 mm each)
- Alignment (rod) phantom (Rod)
- Water Phantom (Water)
- CTP528 High Resolution Line Pair Phantom (Linepair)
- CTP404 Sensitometry Phantom (Sensitom)
- CTP515 Low Contrast Module (LowCon)
- CIRS Edge Phantom (CIRSEP)
- HN715 CIRS Pediatric Head Phantom (CIRSPHP_0)

Experimental Setup

The phase II pCT scanner will be mounted on a bread board, which will be placed on a platform mounted to the robotic positioner in the uniform scanning room at CDH.

The pCT system center will be placed at room isocenter user room alignment lasers. Lateral alignment will be done approximately by eye (for now).

We will run with a 200 MeV proton beam of 4 cm (FWHM) spot size, uniformly scanned using wobbler magnets to the field sizes specified below (at 50% isodose).

The beam intensity will be adjusted the night before the proper runs to approximately 1M protons per sec and spot. Time variations of +/-10% are acceptable.

Run Plan

1. Stepped Scans (stop beam after each projection, transfer data, restart beam for new projection)
- Empty run: 4-5 M histories, field size 12 cm x 36 cm
- Calibration run: 4-5 million histories per brick (0, 1, 2, 3, 4 bricks), field size 12 cm x 36 cm
- Water phantom: one projection, 4-5 M histories, field size 4 cm x 16 cm
- CIRS Edge phantom (CIRSEP): 90 projections, 4 deg intervals, 4-5 M histories per projection, field size 8 cm x 24 cm
- CIRS head phantom: superior and inferior run, each run 90 projections, 4 deg intervals, 4-5 M histories per projection, field size 12 cm x 24 cm
- Water Phantom (Water): 90 projections, 4 deg intervals, 4-5 M histories per projection, field size 4 cm x 16 cm
- CTP404 Sensitometry Phantom (Sensitom): 90 projections, 4 deg intervals, 4-5 M histories per projection, field size 4 cm x 20 cm
- CTP528 High Resolution Line Pair Phantom (Linepair): 90 projections, 4 deg intervals, 4-5 M histories per projection, field size 8 cm x 20 cm
- CTP515 Low Contrast Module (LowCon): 90 projections, 4 deg intervals, 4-5 M histories per projection, field size 8 cm x 20 cm
- Alignment (rod) phantom (Rod): 90 projections, 4 deg intervals, 4-5 M histories per projection, field size 4 cm x 20 cm
2. Radiography Scans:

Data will be acquired in two projections at orthogonal angles (0 deg, 90 deg) to allow for reconstruction of radiographs

- CIRS head phantom: superior and inferior projection, each 2 projections, 90 deg intervals, 8-10 M histories per projection, field size 12 cm x 24 cm
- CIRS Edge phantom (CIRSEP2): 2 projections, 90 deg intervals, 8-10 M histories per projection, field size 8 cm x 24 cm
3. Continuous Scan

This will be done to obtain first experience with a continuous run mode.

- CTP404 Sensitometry Phantom (Sensitom): 90 projections, 4 deg intervals, 4-5 M histories per projection, field size 4 cm x 20 cm

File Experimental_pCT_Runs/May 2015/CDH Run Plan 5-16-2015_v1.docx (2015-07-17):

# Detailed Run Plan for the CDH Beam Test on May 16, 2015

Phantoms (Abbrev.)

- Calibration Phantom (Calib/0) mounted on platform
- 4 additional polystyrene plates (100 x 400 x 50.8 mm each) (Calib/1-4)
- Alignment (rod) phantom (Rod)
- Water Phantom (Water)
- CTP528 High Resolution Line Pair Phantom (Linepair)
- CTP404 Sensitometry Phantom (Sensitom)
- CTP515 Low Contrast Module (LowCon)
- CIRS Edge Phantom (CIRSEP)
- HN715 CIRS Pediatric Head Phantom (CIRSPHP_0)

Experimental Setup

The phase II pCT scanner will be mounted on a bread board, which will be placed on a platform mounted to the robotic positioner in the uniform scanning room at CDH.

The pCT system center will be placed at room isocenter user room alignment lasers. Lateral alignment will be done approximately by eye (for now).

We will run with a 200 MeV proton beam of 4 cm (FWHM) spot size, uniformly scanned using wobbler magnets to the field sizes specified below (at 50% isodose).

The beam intensity will be adjusted the night before the proper runs to approximately 1M protons per sec and spot. Time variations of +/-10% are acceptable.

Run Plan

1. Stepped Scans (stop beam after each projection, transfer data, restart beam for new projection)
- Empty run: 800 MB[^1] histories, field size 12 cm x 30 cm (1.5 A, 3.3 A)
- Calibration run: 800 MB histories per brick (0, 1, 2, 3, 4 bricks), field size 12 cm x 30 cm (1.5 A, 3.3 A)
- Alignment (rod) phantom (Rod): 30 projections, 12 deg intervals, 400 MB histories per projection, field size 12 cm x 8 cm (1.5 A, 1.0 A)
- Water phantom: one projection, 400 MB histories, field size 8 cm x 18 cm (1.0 A, 2 A)
- CIRS Edge phantom (CIRSEP): 90 projections, 4 deg intervals, 400 MB histories per projection, field size 12 cm x 28 cm (1.5 A, 3.0 A)
- Water Phantom (Water): 90 projections, 4 deg intervals, 400 MB histories per projection, field size 8 cm x 18 cm (1.0 A, 2 A)
- CIRS head phantom: superior and inferior run, each run 90 projections, 4 deg intervals, , 400 MB histories per projection, field size 12 cm x 28 cm (1.5 A, 3.0 A)
- CTP404 Sensitometry Phantom (Sensitom): 90 projections, 4 deg intervals, 4-5 M histories per projection, field size 4 cm x 18 cm (0.6 A, 2 A)
- CTP528 High Resolution Line Pair Phantom (Linepair): 90 projections, 4 deg intervals, 4-5 M histories per projection, field size 4 cm x 18 cm (0.6 A, 2 A)
- CTP515 Low Contrast Module (LowCon): 90 projections, 4 deg intervals, 4-5 M histories per projection, field size 4 cm x 18 cm (0.6 A, 2 A)
2. Radiography Scans:

Data will be acquired in two projections at orthogonal angles (0 deg, 90 deg) to allow for reconstruction of radiographs at the time when the stepped scans of each of the two phantoms are completed.

- CIRS head phantom: superior and inferior projection, each 2 projections, 90 deg intervals, 8-10 M histories per projection, field size 12 cm x 24 cm
- CIRS Edge phantom (CIRSEP2): 2 projections, 90 deg intervals, 8-10 M histories per projection, field size 8 cm x 24 cm
3. Continuous Scan

This will be done to obtain first experience with a continuous run mode.

- CTP404 Sensitometry Phantom (Sensitom): long continuous run, field size 4 cm x 20 cm

[^1] As requested by Andriy, we used to have 200 MB of data at LLU

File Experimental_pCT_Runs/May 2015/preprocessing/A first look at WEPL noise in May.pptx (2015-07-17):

## A first look at WEPL noise in May 2015 run at CDH V.A.Bashkirov, June 2nd 2015

Detector noise (background, PMTs, electronics, light leak etc.) looks normal, though there is some additional noise or, most likely, low energy deposition in some cases. Pedestals in MeV have our normal sigma in 0.1-0.16 range, stage 3 is most noisy.

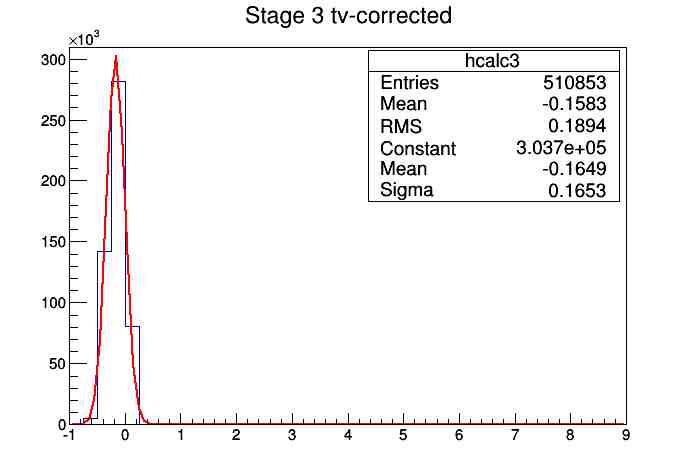
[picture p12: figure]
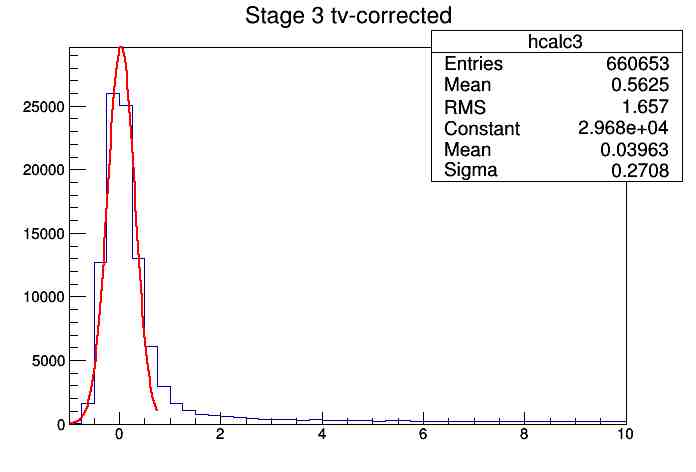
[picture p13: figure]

4briks+step

“empty” (air)

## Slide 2

This “noise”/real low energy deposition results in wrong WEPL, and can be partially suppressed close to stage interface by setting a higher threshold in WEPL reconstruction (presently SetEthresholds(1,1,1,1,1), in MeV), see below events distribution in “empty” run vs WEPL and V ( to show an excess of such events close to top and bottom of the detector)
Thresholds: 0.5, 0.5, 0.5, 0.5, 0.5 1,1,1,1,1 1,1,1,1,4.5

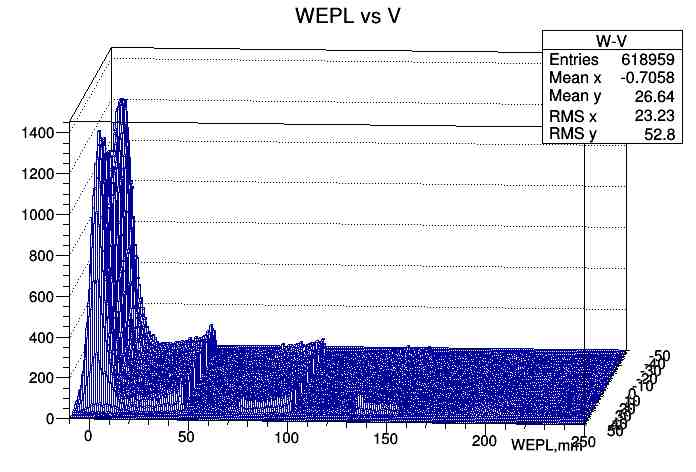
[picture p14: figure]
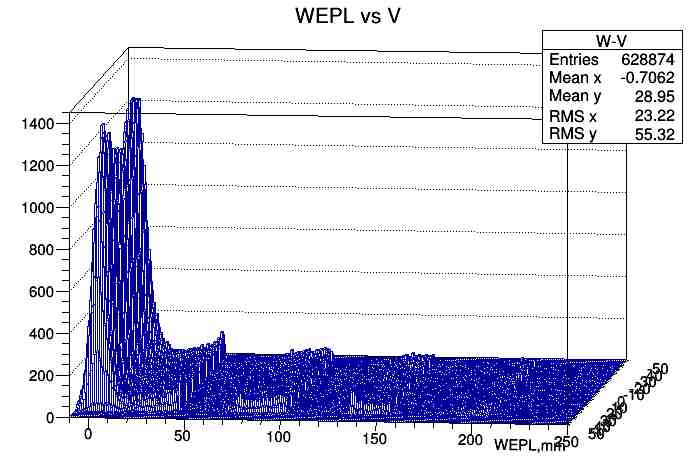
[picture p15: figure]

Thresholds: 1,2,3,4.5.4 1,1,1,4.5,4.5 1,2,3,4.5,5.5

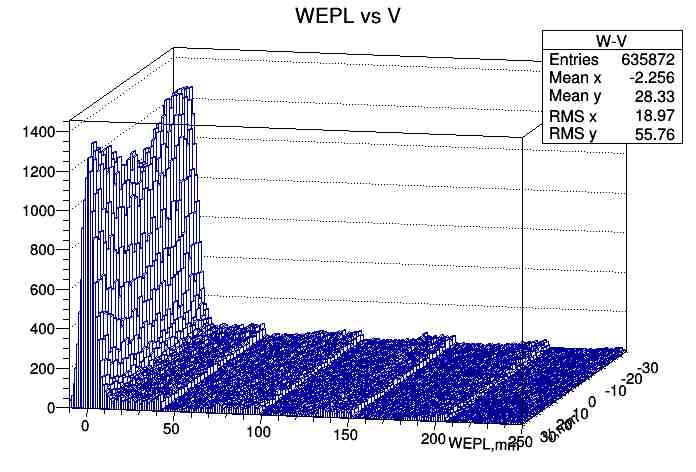
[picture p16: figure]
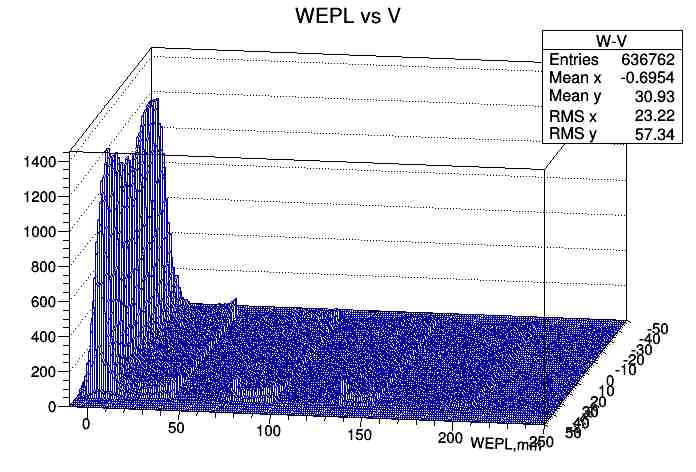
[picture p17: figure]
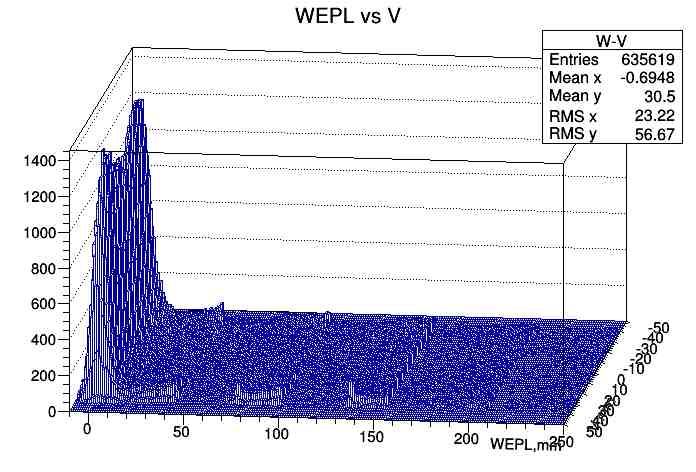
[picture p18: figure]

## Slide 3

Much less of such events occurs when proton stops in the first stage, even at low 0.5 MeV threshold (step+4 briks):

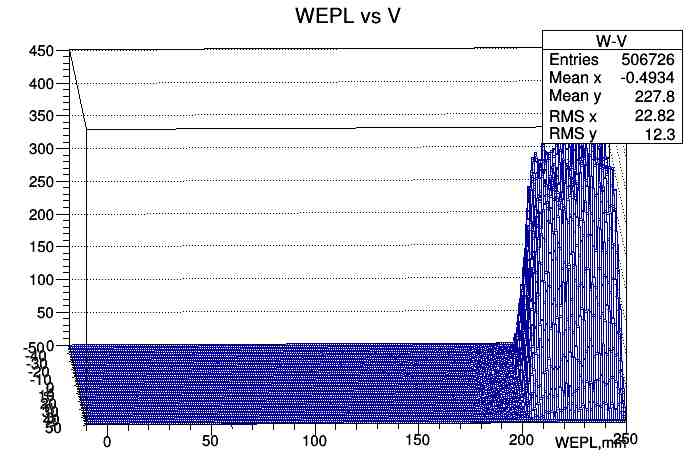
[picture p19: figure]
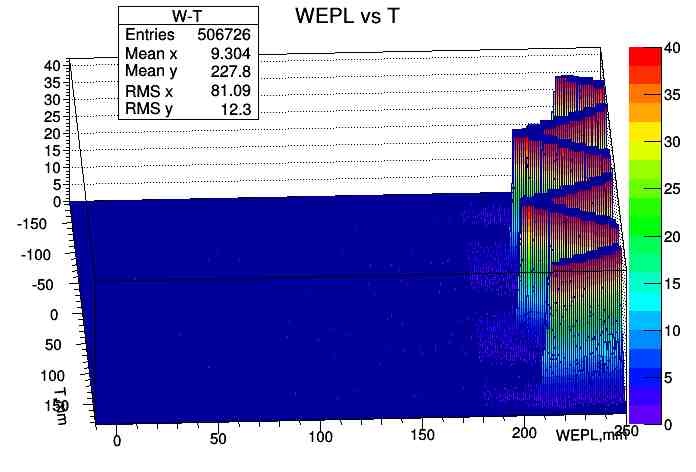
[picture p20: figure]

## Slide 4

For just step phantom, all thresholds 1 MeV we see a lot of “wrong” WEPL events. Low energy proton hallo?

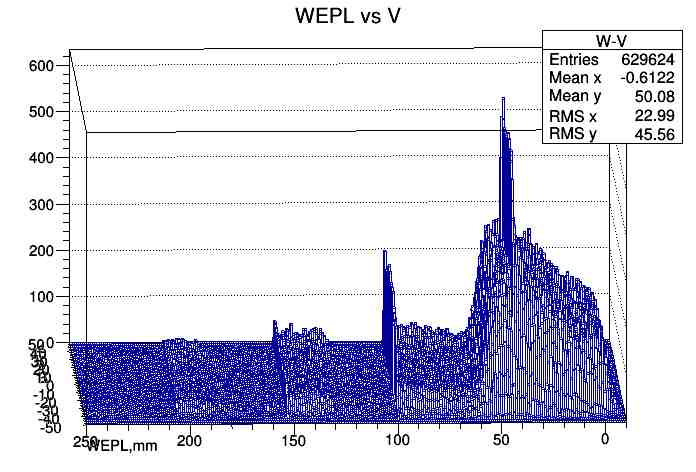
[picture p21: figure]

Thresholds set to 1, 1, 1, 4.5, 4.5 MeV; suppressed peaks at interface of stages 3&4 but most of “wrong” events still there.


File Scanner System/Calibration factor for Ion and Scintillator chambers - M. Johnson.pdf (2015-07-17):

### Calibration factor for Ion and Scintillator chambers

Matthew Johnson
March 5, 2014

### Ion Chamber Factor

For an ion chamber, the basic equation for dose is as follows:

(Charge − background) × Kt,p × ChamberF actor = Dose | (1)

Two background measurements were performed, to

Run Charge(nC) Time (s)
1 | -0.22 | 600
2 | -0.23 | 600

Kt,p is the correction factor for temperature and pressure, and is as follows:

Kt,p =

273 + T
295

×

760
P

(2)

On February 14, 2015 the temperature was 18.0

◦C, and the pressure was 732.4 mm-Hg.

The Ion chamber’s cal factor was determined by comparing the relative output of Loma Linda’s T1 ion chamber and the Farmer chamber. This was done in Gantry 1, with both chambers at center of modulation (60 mm modulation profile), using 149 MeV with 13 cm aperture at 100% intensity.

LLU’s T1 chamber | -4.728 nC 301.7 MU
pCTs Farmer chamber -14.836 nC 86.01 MU

Using equation 1, normalizing charge to MUs, and using the Standards chamber factor of 61.83 cGy/nC, the calibration factor for the pCTs Farmer style chamber is 5.605 cGy/nC. The calibration certificate for 60Co (P=760.0, T=22.0

| ◦C) is 5.391 × 10⁷ Gy/C.

Two does runs were done with the ion chamber, the second run had better timing.

1st ion chamber run. -2.22 pC in 60seconds. 0.0120 cGy/min. 2nd ion chamber run. -2.57pC in 60 seconds, 0.0146 cGy/min.

### Scintillator Chamber Factor

For the scintillator’s calibration factor, Runs 19 and 21 were compared. The sum of the signals in the scintillator’s profile was -200715740, with 13,633,572 events. The events counted for the ion chamber run 16,257,850.
We’re getting the distribution with Pier’s program, taking raw data of run.
1. Evaluate pedestal
2. Subtract pedestal
3. Calculate area excluding pedestal + pedestal area
ADC = CalibrationF actor × Dosep⁺ + P edestal | (3)
Dosep⁺ = (ADC − pedestal)/CalibrationF actor | (4)

Dosetot =

#protons

X

i=1

Dosep⁺ = Nprotons × Dosep⁺ | (5)

Where Dosep⁺ is the average dose deposited per proton. The dose for the Ion chamber can be expressed similarly:

DoseIonChamber = NprotonsIC × Dosep⁺ | (6)

We know dosetot for ion chamber measurements, and can equate them. The calibration factor for the Scintillator is 6.0998E-011 cGy/signal.

signal
Entries | 1.363357e+07
Mean | −884.6
RMS | 1168
Underflow | 0
Overflow | 1840
Integral | 2.269e+05
−4000 | −3000 | −2000 | −1000 | 0 | 1000 0

200

400

600

800

1000

1200

1400

1600

1800

signal
Entries | 1.363357e+07
Mean | −884.6
RMS | 1168
Underflow | 0
Overflow | 1840
Integral | 2.269e+05

## signal

# signal

6 10

Entries 6816784; Mean; RMS; signal

Log plot of ADC signal to show pedestal with Scintillator calibration area.

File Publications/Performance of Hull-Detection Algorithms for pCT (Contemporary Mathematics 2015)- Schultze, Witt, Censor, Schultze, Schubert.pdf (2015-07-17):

This is a free offprint provided to the author by the publisher. Copyright restrictions may apply.

Contemporary Mathematics (http://www.ams.org/conm/)
Volume 636, 2015
http://dx.doi.org/10.1090/conm/636/12739

### Performance of Hull-Detection Algorithms for Proton Computed Tomography Reconstruction

Blake Schultze, Micah Witt, Yair Censor, Reinhard Schulte, and Keith Evan Schubert

Abstract. Proton computed tomography (pCT) is an imaging modality developed for patients who are receiving proton radiation therapy. The purpose of this work was to investigate hull-detection algorithms used for preconditioning of the large and sparse linear system of equations that needs to be solved for pCT image reconstruction. The hull-detection algorithms investigated here included silhouette/space carving (SC), modified silhouette/ space carving (MSC), and space modeling (SM). Each was compared to the cone-beam version of filtered backprojection (FBP) used for hull-detection. Data for testing these algorithms included simulated data sets of a digital head phantom and an experimental data set of a pediatric head phantom obtained with a pCT scanner prototype at Loma Linda University Medical Center. SC was the fastest algorithm, exceeding the speed of FBP by more than 100 times. FBP was most sensitive to the presence of noise. Ongoing work will focus on optimizing threshold parameters in order to define a fast and efficient method for hull-detection in pCT image reconstruction.

### 1. Introduction

Proton computed tomography (pCT) has the potential to become a preferred imaging modality for the planning of proton radiation therapy because images reconstructed from pCT data predict the range of proton beams in the patient more accurately than those obtained from x-ray CT data [Smi09].
The data produced by a pCT scanner are energy measurements of individual protons traversing the object from many different directions. These energy measurements are then converted to water-equivalent path length (WEPL). “Water-equivalent” in this context means that if the proton has the given path-length in water, it will, on average, lose the same amount of energy that the proton has lost

2010 Mathematics Subject Classification. Primary 92C55, 94A08, 68U10; Secondary 65F50, 68W10, 03E75.
Schubert, Schulte, Schultze, and Witt were partially supported by Grant No. 1R01EB013118-01 from the National Institute of Biomedical Imaging and Bioengineering at the National Institutes of Health and the National Science Foundation. The content of this paper is solely the responsibility of the authors and does not necessarily represent the official views of the National Institute of Biomedical Imaging and Bioengineering or the National Institutes of Health.
Censor and Schulte were partially supported by Grant No. 2009012 from the United States -Israel Binational Science Foundation (BSF).
c 2015 B. Schultze, M. Witt, Y. Censor, R. Schulte, K. E. Schubert

211

212 | B. SCHULTZE, M. WITT, Y. CENSOR, R. SCHULTE, AND K. E. SCHUBERT

by traversing the object. From this data, one can reconstruct the relative stopping power (RSP) of protons with respect to water by the formula RSP = Smat/Swater, where the stopping power of a material, Smat = −dE/dx, is the mean differential energy loss (dE) of protons per unit path length (dx). The image reconstruction of pCT requires finding a computationally tractable solution to a large and sparse linear system of equations of the form Ax = b, where the matrix A contains the proton path information, i.e., the index of the object voxels intersected by the path, the vector b contains the WEPL values, and the solution vector x contains the RSP values in voxels after the system has been solved.
High-speed performance and accurate reconstruction are important prerequisites for clinical applicability of pCT. The size of the linear system, which is of the order of 10⁸ × 10⁷, requires a parallelizable iterative image reconstruction algorithm to be implemented across a multi-processor, e.g., a graphics processing unit (GPU), computing cluster. Recent studies demonstrated that good quality pCT images can be reconstructed with iterative projection algorithms performed on a single GPU [Pen10,PSCR10].
Efficient image reconstruction can be significantly expedited if accurate knowledge of the object’s hull is available. For an object X ⊂ N³, which is a finite set of voxels, and a discrete image space V ⊂ N³ defined such that X ⊆ V , we define the object’s hull, H, as the smallest subset H ⊆ V such that X ⊆ H; in other words, the hull is the the smallest bounded region that encloses the object. The object’s hull, H, is needed for the most likely path (MLP) calculations, which is an important step in pCT image reconstruction [SPTS08].
With an accurate hull-detection algorithm, any voxel outside the hull can be excluded from image reconstruction, effectively reducing the size of x and, thus, the number of columns of A. Iterative solutions of a linear system with m rows (proton histories) and n columns (voxels) has time complexity O(mnk), where k is the number of iterations. In a pCT system, typically 100n ≥ m ≥ 10n. However, a proton passes through the largest number of voxels when it traverses the reconstruction volume diagonally, corresponding to approximately √3 n voxels. Thus, the system matrix, A, only contains on the order of √3 n non-zero elements

and, consequently, O(mnk) reduces to O(n¹.333k). The memory requirements for the parallel iterative image reconstruction algorithms also decrease as the number of voxels misidentified as part of the hull is reduced. This is particularly important in a GPU system. An efficient hull-detection algorithm reduces the execution time of pCT image reconstruction. Therefore, the objective of the hull-detection algorithms for pCT is to efficiently produce an accurate approximation of the hull.
In this work, we report on hull-detection using two established algorithms, i.e., filtered backprojection (FBP) and silhouette/space carving (SC) and two new algorithms, i.e., modified silhouette/spacecarving (MSC) and space modeling (SM) that we developed for pCT image reconstruction.

### 2. Data Characteristics

The data used in this work came from two sources. Initial data testing was done using a simulated digital phantom designed for pCT [WSS12]. Advanced testing was done on an actual scan of a pediatric head phantom using the Phase I prototype pCT scanner at Loma Linda University Medical Center [HSB12,HSBC12]. The simulated and scanned data sets are described in the following sections.

PERFORMANCE OF HULL-DETECTION ALGORITHMS | 213

### 2.1. Simulated Phantom. The phantom input data used to assess the per-

formance of each hull-detection algorithm was produced using a pCT simulator specifically designed for algorithm analysis [WSS12]. The simulator provides the user with the ability to construct a non-homogeneous elliptical object (NEO) to approximate head phantoms of various sizes and with simplified representations of anatomical features, such as ventricles, frontal sinus, ears, and nose.
The specific digital phantom used in this work is shown in Figure 1; the phantom had an isotropic voxel size of 1 mm³ and was comprised of an outer elliptical region representing skull bone enclosing brain and two inner elliptical sections representing fluid-filled ventricles. These regions were assigned realistic RSP values: 1.6 for bone, 1.04 for brain, and 0.9 for ventricles.


Figure 1. Digital head phantom used to generate simulated data in this work. (Figure 1 originally appeared in “Space carving and filtered back-projection as preconditioners for proton computed tomography reconstruction”, by B. Schultze, et al., published in Nuclear Science Symposium and Medical Imaging Conference (NSS/MIC), 2012 IEEE, October 27–November 3, 2012. Reprinted with permission.)

Two simulated data sets were produced to assess the hull-detection algorithms presented in this paper, each with a total of 11,796,480 proton histories. The first simulation in this study generated a uniform beam of 200 MeV protons. Each proton in the beam was randomly distributed about the central beam axis to simulate a realistic proton cone-beam. The simulator also generated bivariate normal random variables for exit angle and displacement with respect to the entry angle and displacement to simulate the effect of multiple Coulomb scattering inside the object. The intersection lengths for the voxels that lay on a proton path were taken to be 1 mm so that the entry in every row of the system matrix was either one or zero. The noiseless WEPL generated for each proton was the sum of the RSP of each intersected voxel. Straight-line paths were assumed between the entry and exit points of the phantom.
The data from the first simulation was duplicated with noisy WEPL values. These were created by first converting a noiseless WEPL value into exit energy, generating a normally distributed noisy energy value with a standard deviation described by Tschalar’s energy straggling theory [T68], and converting that noisy energy value back to a final WEPL value. The conversion of exit energy to WEPL and vice versa was based on ICRU Report 49 [Int93].

214 | B. SCHULTZE, M. WITT, Y. CENSOR, R. SCHULTE, AND K. E. SCHUBERT

### 2.2. Scanner Data. An experimental data set was used in order to assess

the performance of each algorithm with realistic data. This data set contained 50,897,953 proton histories obtained from a scan of an anthropomorphic pediatric head phantom (Model 715-HN, CIRS¹) on the Phase I prototype pCT detector system shown in Figure 2. The scan was obtained using a proton cone-beam of approximately 200 MeV generated by the medical proton accelerator at Loma Linda University Medical Center. The number of proton histories corresponds to a complete data set, i.e., without the removal of unsuitable proton histories. The pediatric head phantom was rotated a full 360◦ with respect to the fixed horizontal beam and pCT detector system in 4◦ increments.


(a) (b)

Figure 2. (a) A pediatric head phantom being rotated (curved arrow) with respect to the fixed horizontal beam (straight arrow) on the Phase I prototype pCT scanner at Loma Linda University Medical Center. (b) pCT reconstruction of a representative slice of the pediatric head phantom. (Figure 2(b) is from “Overview of the LLUMC/UCSC/CSUSB Phase 2 Proton CT Project”, by
R. W. Schulte et al., published in Transactions of the American Nuclear Society, vol. 106, Chicago, IL, June 24–28, 2012. c 2012 American Nuclear Society, La Grange, IL. Reprinted with permission.)

Some of the proton histories may not be suitable for pCT image reconstruction, including hull-detection. One source of unsuitable proton histories in our present data sets was pile-up due to protons arriving at the energy detector (calorimeter) too closely in time, thus causing the residual energy from the first proton to be added to the energy measurement of the second proton. Other unsuitable proton histories were excluded from the pCT image reconstruction because they underwent atypical physical interactions, including elastic large angle scattering and inelastic nuclear interactions.
Unsuitable data resulting from pile-up and atypical physical events can be removed by grouping (binning) histories into intervals with similar angle and similar horizontal and vertical displacement relative to the center of the reconstruction volume. Histories whose WEPL, relative horizontal angle, or relative vertical angle

1http://www.cirsinc.com/products/all/36/pediatric-anthropomorphic-trainingphantoms/?details=specs are beyond three standard deviations from the mean of each bin are then removed from the data set (data cuts).

### 3. Hull-Detection Algorithms

For an object X ⊂ N³ with hull H ⊆ V ⊂ N³, a hull-detection algorithm seeks an approximate hull, H ⊆ V , such that H ⊆ H and the cardinality, |H \ H|, of the set difference, H \ H, is as small as possible. In essence, we seek to produce an approximation of the hull which contains every voxel of the object while minimizing the number of voxels included from outside the object.
Three algorithms were tested in this work and compared to filtered backprojection (FBP): silhouette/space carving (SC), modified silhouette/space carving (MSC), and space modeling (SM). FBP is capable of performing a full image reconstruction; however, protons follow curved paths due to multiple Coulomb scattering, which does not fit the reconstruction framework of FBP. Here, FBP was used to detect an approximate hull and to generate the starting data set for the iterative reconstruction algorithm, as done in previous pCT reconstruction work [Pen10, PSCR10]. In previous work on hull-detection algorithms for pCT reconstruction, we had compared SC to FBP with respect to computation time and quality [SWSS12], but that comparison did not include a voxel-by-voxel comparison between the true and the detected object hull.

### 3.1. Filtered Backprojection (FBP). FBP is a well-known algorithm, first

introduced for reconstruction of CT data by Ramachandran and Lakshminarayanan [RL71]. In this work, we used the Feldkamp Davis Kress (FDK) algorithm [FDK84], a cone-beam variant of the FBP algorithm, assuming that all proton paths through the object were straight lines and followed a cone-beam geometry. The FDK algorithm was performed with 4◦ angular bin spacing, a 1 mm lateral bin size, and a 5 mm vertical bin size. Each slice of the reconstruction volume was defined to be 200 mm × 200 mm and 3 mm thick. With this thickness and a reconstruction volume height of 9.6 cm, a total of 32 slices were produced. A Shepp-Logan filter [SL74] was used prior to backprojection. The resulting image was then thresholded to generate the approximate hull. Any voxel with RSP ≥ 0.6 was assumed to belong to the object and was assigned an RSP value of one. Voxels with RSP values below this threshold were assigned an RSP value of zero.
In this work, FBP was performed for hull-detection using the proton histories that remained after data cuts were performed to remove unsuitable proton histories. The data cuts were performed on the proton histories after binning them into the intervals described above.

### 3.2. Silhouette/Space Carving (SC). SC is an algorithm used to generate

an approximation of the object’s hull in a similar way that sculptures are chiseled from a solid block of material [Nie94, Nie97, KS99]. If a proton does not pass through the object, it will not experience significant energy loss or scattering. Therefore, individual or bin-averaged energy measurements (or, alternatively, converted WEPL values) and angular deviations can be used, in principle, to identify which protons missed the object entirely. Protons that missed the object are identified by placing a cutoff value on energy measurements (or WEPL values) and angular deviations such that, if the measured values fall below the cutoff values,

216 | B. SCHULTZE, M. WITT, Y. CENSOR, R. SCHULTE, AND K. E. SCHUBERT

then the proton or all protons associated with a proton bin are assumed to have missed the object.
Initially, the object is assumed to encompass the entire reconstruction volume and each voxel is assigned an RSP value of one. If a proton is identified as having missed the object, the voxels along its path, approximated by a straight line, are carved from the reconstruction volume by assigning them an RSP value of zero. Note that a straight line is an accurate approximation of the path due to the insignificant amount of scattering in air. The voxels that are not carved from the reconstruction volume and, thus, retain an RSP value of one, are then assumed to belong to the object hull.
SC (see Algorithm 1 below) seeks an approximation, H1, of the hull, H, by identifying the protons that missed the object based on analysis of WEPL values and then carving the voxels along each of their paths from the reconstruction volume. In other words, for each projection angle in the scan, projecting the paths of protons that miss the object through the reconstruction volume produces a silhouette of the object where no proton passed through. Excluding the voxels outside these backprojected silhouettes then yields an approximate object hull. Notationally, pi refers to the i
| th proton or proton bin, ΔE(pi) refers to the
energy loss of the i
| th proton or the mean energy loss of protons in bin i, respectively,
and Δ∠(pi) is the change in angle of the i
| th proton or the mean change in angle of
protons in bin i, respectively. Let I be the set of indices of all the protons or proton bins. Let EL be the user-defined cutoff value on the energy lost in air and θL be the user-defined cutoff value on the angular change of protons in air. If ΔE(pi) and Δ∠(pi) fall below their associated cutoff values, then the proton or protons assigned to the proton bin, pi, are assumed to have missed the object. We then define the set, IL, of indices of these protons or proton bins as
(3.1) IL = {i ∈ I | ΔE(pi) <EL, Δ∠(pi) <θL} .

Let V be the set of all voxels in the reconstruction space. Let Li be the line that connects the entry and exit points of the proton or protons assigned to the proton bin with index i, for i ∈ IL. Given a distance measure d(·, ·) and a minimum distance d0, we define the set, Ai, of voxels along the path, Li, as

Ai = {v ∈ V | d(Li (3.2) | ,v) ≤ d0}

and the approximate hull is then given by

H1 = V \∪i∈IL Ai (3.3) | .

In this work, the implementation of the SC algorithm used the proton histories that remained after data cuts were performed to remove unsuitable proton histories. The bin size for the data cuts was the same as that used for the FDK algorithm. The same bins were also used to define the paths, Li, in the SC algorithm. A cutoff value on the mean WEPL of a bin, rather than on the energy loss, was used to identify protons that missed the object; if the mean WEPL of a bin was less than 1.0 mm, the protons in that bin were assumed to have missed the object and the voxels along their path, approximated by a straight line using the angle and displacements associated with that bin, were carved from the reconstruction volume. No angular cutoff was used in this implementation of the SC algorithm.

Algorithm 1 Silhouette/Space Carving (SC)

1: IL ←∅
2: for all i ∈ I do
3: | if ΔE(pi) <EL and Δ∠(pi) <θL then
4: | IL ←{IL,i}
5: | end if
6: end for
7: for all v ∈ V do
8: H1(v) ← 1
9: end for
10: for all i ∈ IL do
11: | for all v ∈ V do
12: | if d(Li,v) ≤ d0 then
13: | H1(v) ← 0
14: | end if
15: | end for
16: end for

To avoid excluding valid portions of the object from the detected hull due to unsuitable proton histories evading data cuts and protons skimming the surface of the object, a simple 5×5 averaging filter was applied to the image of the approximate hull. The approximate object hull was then formed from the filtered image by assigning voxels a value of one if their value exceeded a threshold of 0.4 (a tunable parameter) and assigned a value of zero otherwise.

### 3.3. Modified Silhouette/Space Carving (MSC). SC does not record

the number of times, N, a voxel was determined to lie outside the boundary of the object; thus, voxels belonging to the object can mistakenly be excluded from the detected hull due to the presence of unsuitable data. MSC is a new hull-detection algorithm proposed here which uses the number of times, N, a voxel was identified as lying outside the object to determine which voxels should be excluded from the approximate hull. Since unsuitable proton histories make up a relatively small percentage of the total proton histories, they will have minimal effect on N for a particular voxel. Therefore, by considering N, MSC can theoretically avoid mistakenly excluding voxels belonging to the object from the detected object hull. MSC (see Algorithm 2 below) seeks to robustly generate an approximation, H2, of the hull, H, by backprojecting the silhouette and counting the number of times, N, a voxel is marked outside the silhouette. Note that MSC uses only the proton histories that did not pass through the object. We then define the set, C(v), of indices of the paths, Li, that passed through voxel v as

(3.4) C(v)= {i ∈ IL | v ∈ Ai}

and the set, B(v), of neighboring voxels, w, of voxel v as

(3.5) B(v)= {w ∈ V | d(v, w) ≤ 1} .

Defining the cardinality of C(v) as N(v)= |C(v)|, the cardinality of C(w) as N(w)= |C(w)|, and given a minimum cardinality difference threshold Nt, the

218 | B. SCHULTZE, M. WITT, Y. CENSOR, R. SCHULTE, AND K. E. SCHUBERT

approximate hull is then defined as

H2 =

v ∈ V

max
| w∈B(v)

N(v) − N(w) <Nt

(3.6) .

Algorithm 2 Modified Silhouette/Space Carving (MSC)

1: IL ←∅
2: for all i ∈ I do
3: | if ΔE(pi) <EL and Δ∠(pi) <θL then
4: | IL ←{IL,i}
5: | end if
6: end for
7: for all v ∈ V do
8: | H2(v) ← 1
9: | N(v) ← 0
10: end for
11: for all i ∈ IL do
12: | for all v ∈ V do
13: | if d(Li,v) ≤ d0 then
14: | N(v) ← N(v)+1
15: | end if
16: | end for
17: end for
18: for all v ∈ V do
19: | for all w ∈ B(v) do
20: | if N(v) − N(w) ≥ Nt then
21: | H2(v) ← 0
22: | end if
23: | end for
24: end for
| In this work, the implementation of the MSC algorithm did not include perform-
ing data cuts to remove unsuitable proton histories. Decisions on whether protons missed the object were based on analysis of individual WEPL values rather than bin averages. Thus, proton histories were not binned in this case. Proton histories whose WEPL values were less than 1.0 mm were assumed to have missed the object, which is the same WEPL cutoff value used for SC. A threshold Nt = 50 was used here as this was found to be insensitive to the varying number of proton histories in each data set. Note that a cardinality threshold proved to be an inadequate basis for identifying voxels outside the object hull, as an appropriate cardinality threshold varied between slices and data sets. However, the cardinality difference, N(v) − N(w), between neighboring voxels proved to be a more robust measure.
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

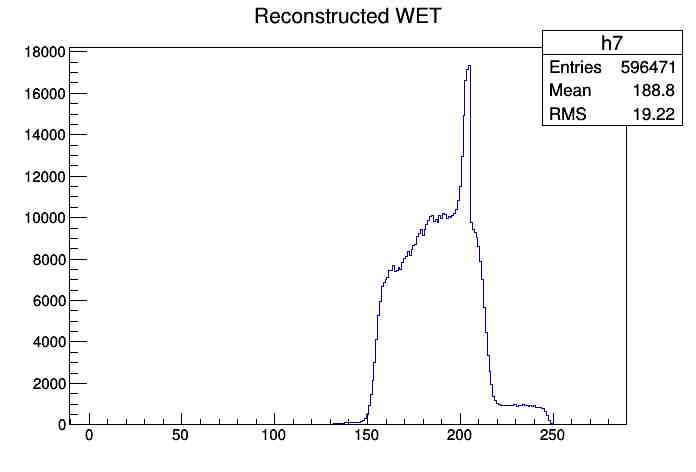
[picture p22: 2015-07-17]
Experimental_pCT_Runs/May 2015/preprocessing/Wr3.jpg

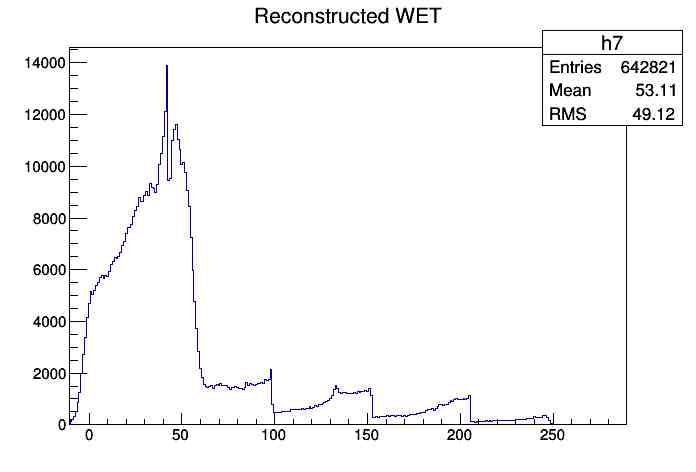
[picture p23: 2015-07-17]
Experimental_pCT_Runs/May 2015/preprocessing/Wr0.jpg

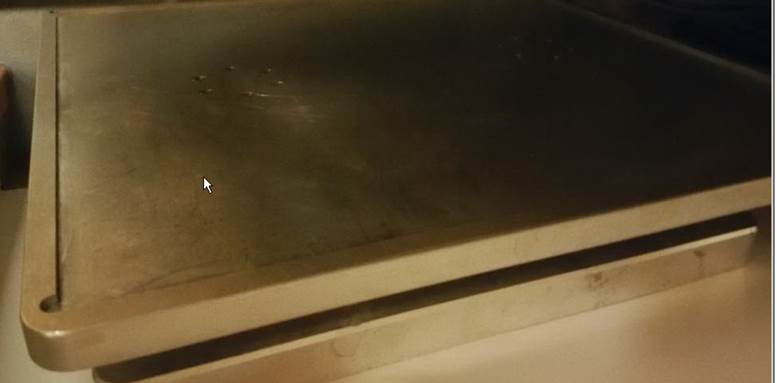
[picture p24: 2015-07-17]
Experimental_pCT_Runs/May 2015/Run pictures/robotic positioner platform.jpg

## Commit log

2015-05-09 Added pCT Data Naming/Organizational Format
    Documents showing hierarchical structure of pCT data storage and
    file/directory naming scheme. This format is shown visually in 1 PDF
    and an explanation of each of the files/folders shown is given in
    another PDF. Note that the current version of the visual representation
    of the format has the hierarchy under "Experimental" cut off, but its
    subdirectories should match those under the GEANT4 and TOPAS hierarchies
    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
2015-07-17 Updated format and fixed PDF diagram
    format updates:
    - Changed date format from MMDDYYYY to YY-MM-DD so lexicographic
    ordering organizes by date with year first and adding dashes between
    parts makes reading/interpreting dates easier
    - Changed run # format from "Run_XXX" to "XXX[_AAA]" removing the
    unnecessary inclusion of the word "Run" which is also not included in
    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
2015-07-17 Added files and subdirectories for publications and theses/dissertations
    Added some pCT information files and added a number of
    theses/dissertations and papers along with subdirectories where these
    will be stored separately
    [Phase II pCT.xlsx, pCT phantoms.xlsx]
2015-07-17 Added data distribution list of people
    [Data distribution list.xlsx]
2015-07-17 Added more files
    Added the various phantom images and pCT documentation from Dropbox
    folders
    [pCT phantoms.xlsx]
2015-07-19 Updated pCT data format tex/PDF from Kodiak
    [Data distribution list.xlsx, Phase II pCT.xlsx, pCT phantoms.xlsx]
2015-07-20 Added directory usage descriptions
    Added an outline of the relevant directories local to each Kodiak/Tardis
    cluster nodes and the directories on the network storage drive mounted
    on Kodiak/Tardis making its contents accessible from each of the
    master/compute nodes.
2015-07-26 Updated/modified phantom ID and object folder naming schemes and data distribution users
    Finished the Excel file that lists the phantom ID used to name raw data
    files for each phantom currently in possession of the collaboration and
    the corresponding object folder name to use for storing/organizing the
    data for each of these phantoms. This file also outlines the additions
    to the naming scheme used for non standard scan configurations such as
    superior/inferior scans of the head phantom and for continuous scans,
    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
    [Data distribution list.xlsx, pCT phantoms.xlsx, pCT_Data_Hierarchy.dwg, pCT_Data_Users.xlsx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]
2015-08-01 Update data hierarchy diagram
    updated diagram
    [pCT_Data_Hierarchy.dwg]
2015-08-07 Modified pCT experimental file naming file
    After 07/25/15 run, some changes were made to the way files will be
    named during the scan, although the naming scheme used did not conform
    to the format established prior to the run. These are minor changes
    made in an attempt to come closer to the naming scheme that was used at
    the time of the run which is clearly what feels more natural when
    creating them. These are minor changes.
    [pCT_Data_Hierarchy.dwg, pCT_Phantom_List.xlsx]
2016-02-07 Updated to reflect data move from \data\ion to \ion
    Since the last commit, the directory \ion dedicated to proton and ion
    therapy is no longer a subdirectory of /data but was moved up one
    directory so that it is stored at the top level of the Baylor server
    network mounted hard disk.
2016-02-11 pCT data format update
    Continued modifications to reflect Kodiak storage directory moves and
    expanded descriptions of data directories including relevant information
    related to other developments
    [pCT_Phantom_List.xlsx]
2016-07-21 Updated/improved documentation files, particularly the code/data naming/organizational scheme documentation
    [pCT_Collaborators.xlsx, pCT_Data_Hierarchy.dwg, pCT_Data_Users.xlsx, pCT_Scanner_Phase_II.xlsx]
